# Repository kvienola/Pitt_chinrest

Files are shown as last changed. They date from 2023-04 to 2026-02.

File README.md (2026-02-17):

# A modular chinrest for retinal imaging

The main function of this repository is to distribute the component designs of the original chinrest. Everything is free to download and we only ask you to cite our paper XXX if you decide to use the chinrest design (or part of it) in your scientific setup.

The headrest was designed to be modular and most of the parts are 3D printable to minimize manufacturing costs. I roughly categorized the subassemblies/parts into few categories to quickly explain the reason behind the design decision and the material we chose. This is our first prototype so if you have ideas for design improvements, you can modify these parts as you please.

If you wish to have the master assembly file from Fusion 360, please contact Kari Vienola. Also if you find the chinrest files useful, consider citing our paper: http://dx.doi.org/10.1364/AO.513801 (Head stabilization apparatus for high-resolution ophthalmic imaging).

Kari V. Vienola  
_Academy Research Fellow_  
_University of Turku_

Ethan A. Rossi  
_Assistant Professor_  
_University of Pittsburgh_

## Contents

Detailed description of what is in each folder

### Mounting

As we are using Velmex motorized stages for all three axes of motion, the current base plate for mounting is quite large. The mounting plate size can be modified if you keep the hole distances in the bottom the same. The two mounting brackets are made from aluminum mainly so that they can be securely mounted to the base with threaded holes.

Material used: MIC6 cast aluminum, ½” thickness

### Chinrest

This consists of two parts, the sliding guide that is mounted to the base and the chinrest piece itself. The chinrest piece was designed to be moved along the z-axis (parallel to the optical axis of the incoming beam) to accommodate different head shapes. The “cupping” for the chin was done by trial and error and it can be altered if needed. Gluing a thin rubber in the chin cup will increase the friction as some 3D printed plastics might be a bit slippery. The bottom has a slot insert for metal piece that is inserted either a) gluing or b) heating up the metal piece and allowing the surrounding plastic to melt. This metal piece is meant to protect the plastic from the locking screw (not mandatory but highly suggested). The length of the dove rail can be easily extended by extruding the piece itself.

Material/parts used: standard 3D printing plastics and scrap metal/aluminum for the slot, brass insert: https://www.mcmaster.com/93738A210/

### Headband

The left and right mounting brackets have t-slots machined in them with slot opening for the screw to tighten the headband to a certain height. The adapter pieces that go inside the t-slot and the headband itself can be 3D printed as one piece but as we were prototyping, we kept them separate in case material had to be changed or the headband diameter would not be correct.
Brass inserts are melted into the headband for proper threads and the bottom hole are used for connecting the t-slot pieces with the headband. The top holes are for the screw that goes through the mounting bracket and locks the headband in place for the desired height.
Materials used: standard 3D printing plastic, brass inserts, screws to clock the band in place

### Forehead slider
The forehead slider consists of 4 pieces: tapered nut, the slider itself, the rod and the temple pad. Originally the idea was to machine the rod, but 3D printed version seemed to work just fine. The tapered nut will squeeze the rod opening the more you tighten it and provides very sturdy locking mechanism. The temple pad is just snapped in place and again, rubber or felt can be glued on to the surface if wanted.

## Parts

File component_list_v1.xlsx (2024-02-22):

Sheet: 3D printed parts
Item | Code | Qty | Printing Material
Tapered nut | RL001 | 2 | Depends on your 3D printer capabilities.
Forehead slider | RL002 | 2
Temple pad | RL003 | 2
Temple pad rod | RL004 | 2
Forehead band | RL005 | 1
Chinrest cup | RL006 | 1
Chinrest slider base | RL007 | 1
T-slot adapters | RL008 | 2

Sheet: CNC machined components
Item | Code | Qty | Material
Mounting bracket left | RL009 | 1 | Aluminum (MICA)
Mounting bracket right | RL010 | 1 | Aluminum (MICA)
Mounting base (custom) | RL011 | 1 | Aluminum (MICA)
Chinrest slider protection | RL012 | 1 | Aluminum (MICA)

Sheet: Off-the-shelf components
Item | McMaster & Carr code | Qty | Material | Usage | Link
Heat-Set Inserts for Plastic | 93738A210 | 5 | Brass | T-slot adapters and chinrest guide | https://www.mcmaster.com/93738A210/
Flat Head Screws | 92210A305 | 2 | Stainless Steel | To attach T-slot adapter to headband | https://www.mcmaster.com/92210A305/
Socket Head Screw | 92196A291 | 2 | Stainless Steel | Clamp headband in place | https://www.mcmaster.com/92196A291/
Srew-Head Mount Knob | 94052A051 | 2 | Plastic | Knob for the headband clamp | https://www.mcmaster.com/94052A051/
Socket Head Screw | 92196A541 | X | Stainless Steel | Universal component mounting (chinrest, vertical brackets) | https://www.mcmaster.com/92196A541/
The length of each component presented here can vary in case you decide to alter the design.
You may also use screws that you have already or different type of plastic inserts.

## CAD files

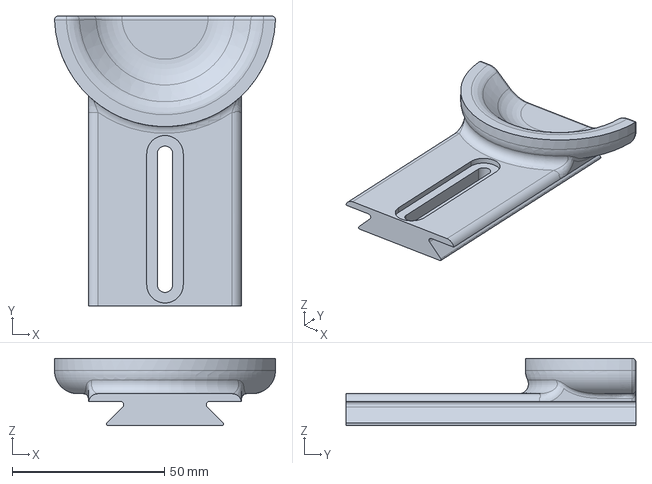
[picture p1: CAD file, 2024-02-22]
chinrest/version_02/chinrest_cup.step
72.6 x 95.2 x 22.1 mm

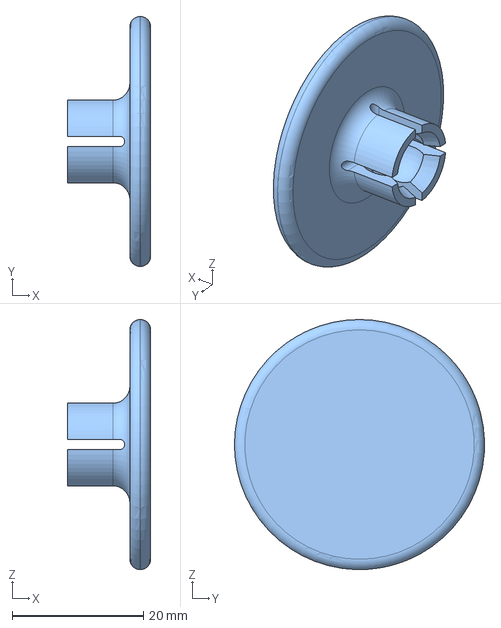
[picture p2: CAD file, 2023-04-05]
forehead slider/temple_pad.step
12.7 x 38.1 x 38.1 mm

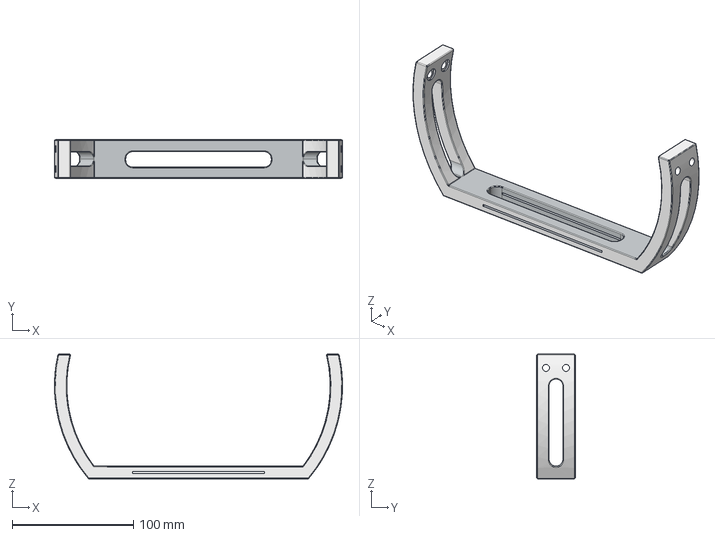
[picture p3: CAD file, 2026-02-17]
headband/headband_Davis_v1.stp
237.5 x 31.8 x 102.7 mm

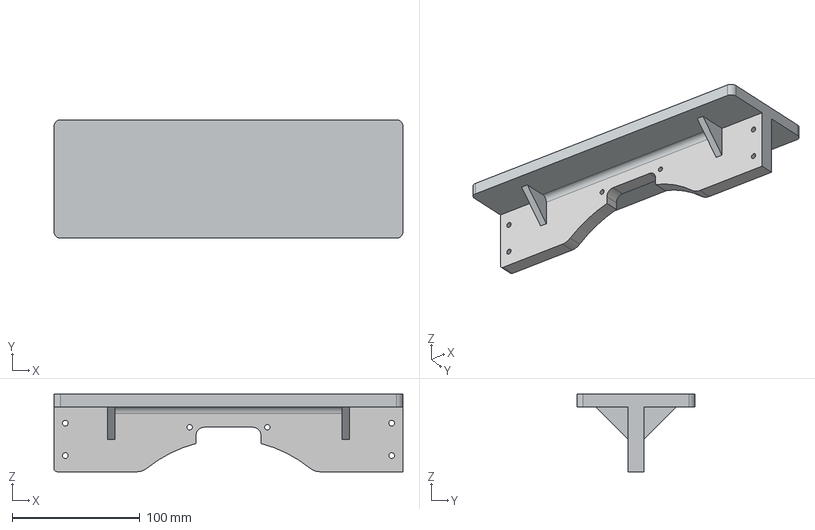
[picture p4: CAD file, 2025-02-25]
mounting/mounting_base_AOSLO_ver2.stp
273.6 x 92.7 x 60.8 mm

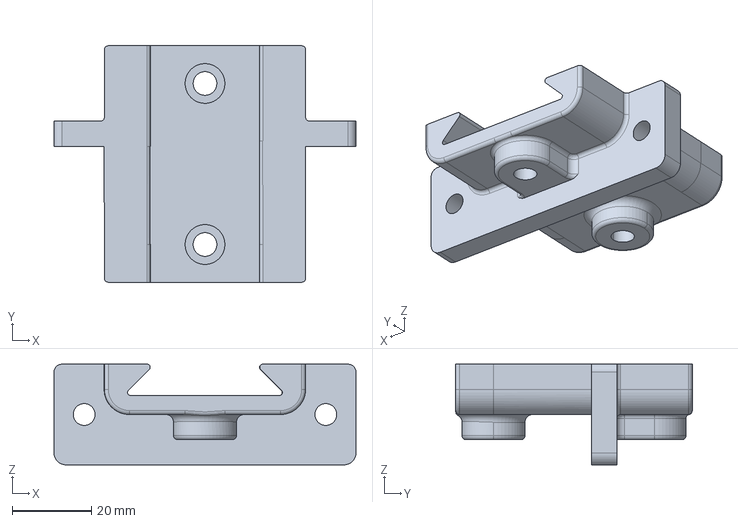
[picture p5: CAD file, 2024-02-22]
chinrest/version_02/chinrest_slider.step
76.2 x 59.7 x 25.4 mm

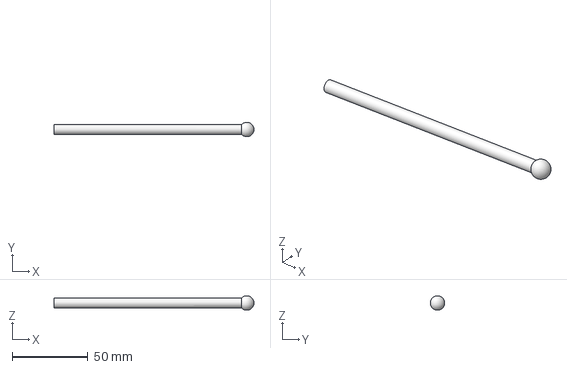
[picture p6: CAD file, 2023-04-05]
forehead slider/slider_rod.step
131.7 x 9.49 x 9.53 mm

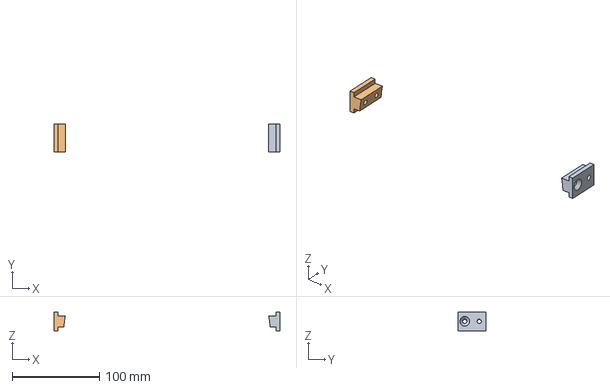
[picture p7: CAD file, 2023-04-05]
headband/detachable_tslots.step
259.7 x 31.8 x 21.6 mm

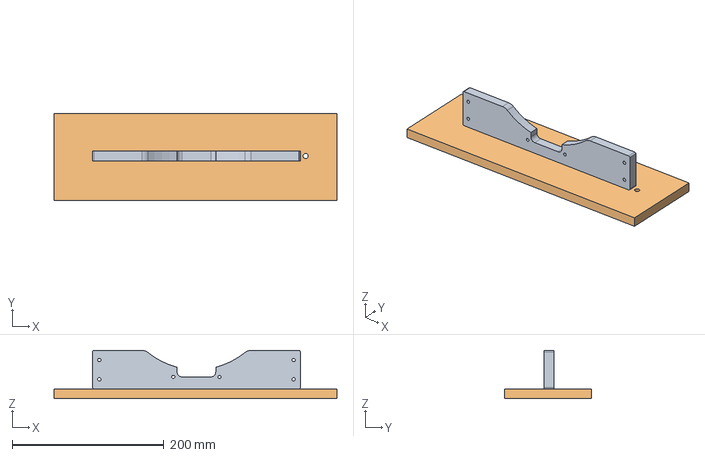
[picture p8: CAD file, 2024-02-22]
mounting/mounting_base_Tracker.step
372.6 x 114.3 x 63.5 mm

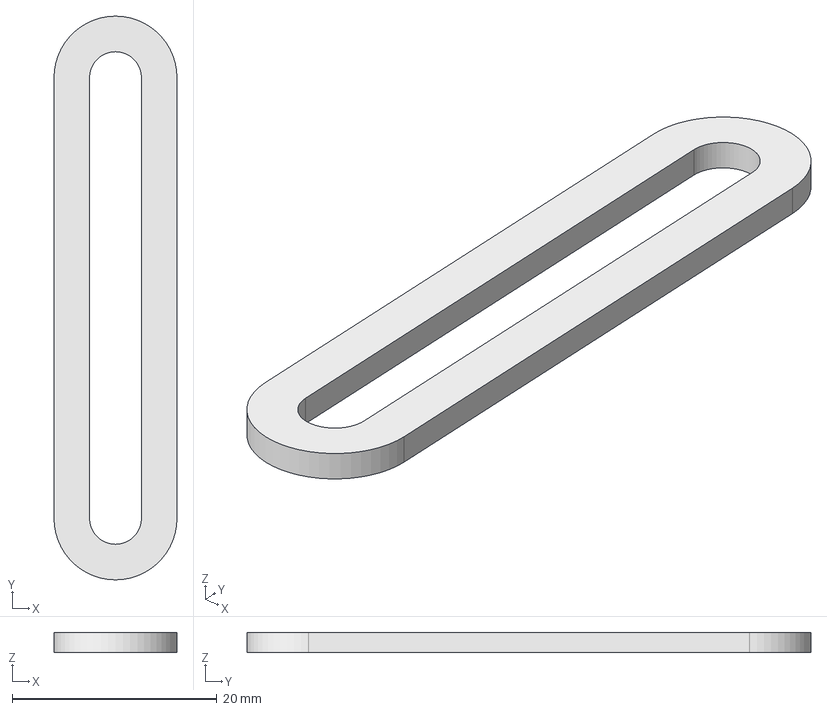
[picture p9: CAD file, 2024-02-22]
chinrest/version_02/metal_insert.step
12.0 x 55.0 x 2.00 mm

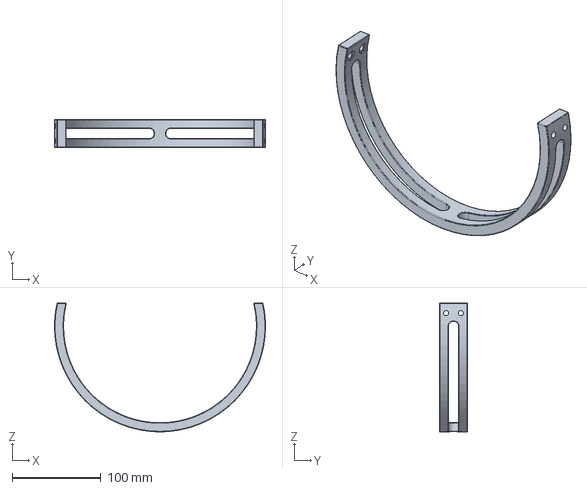
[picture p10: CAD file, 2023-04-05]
headband/headband.step
237.5 x 31.8 x 144.9 mm

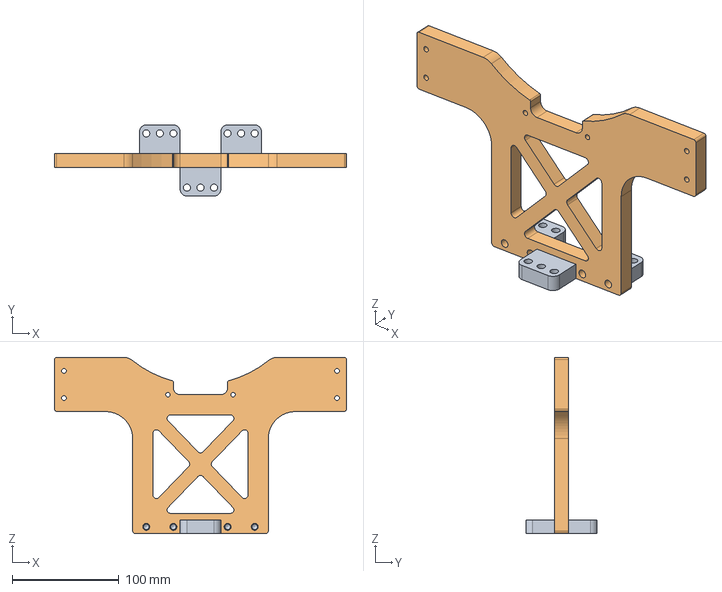
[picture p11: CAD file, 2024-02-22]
mounting/mounting_base_FFOCT.step
273.6 x 66.7 x 165.1 mm
V4 Riser Bracket x 3

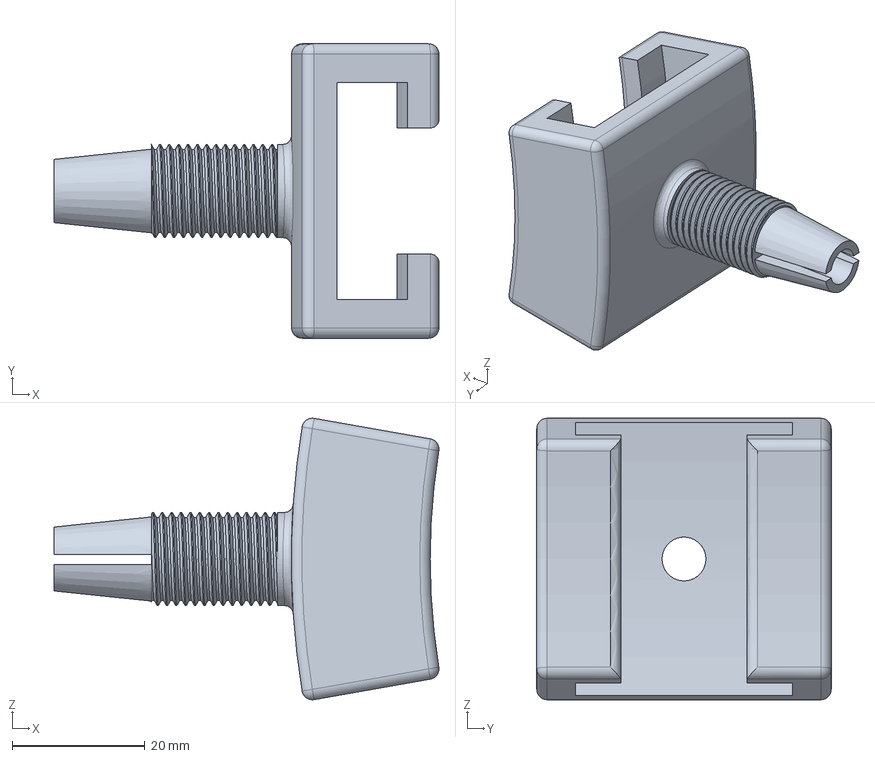
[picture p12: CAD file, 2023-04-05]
forehead slider/slider.step
58.1 x 44.4 x 42.5 mm

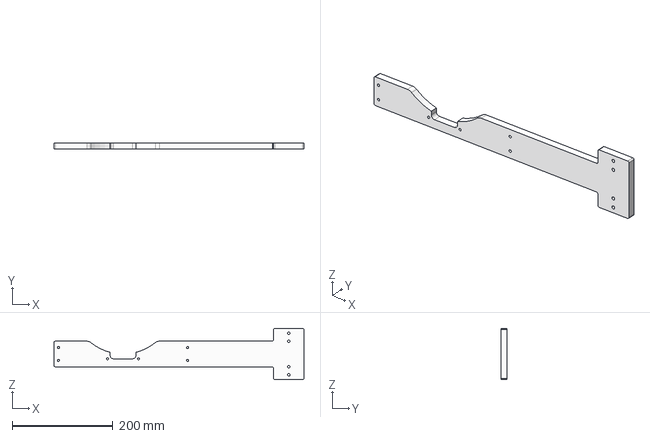
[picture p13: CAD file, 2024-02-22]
mounting/mounting_base_LDH.step
495.3 x 12.7 x 101.6 mm

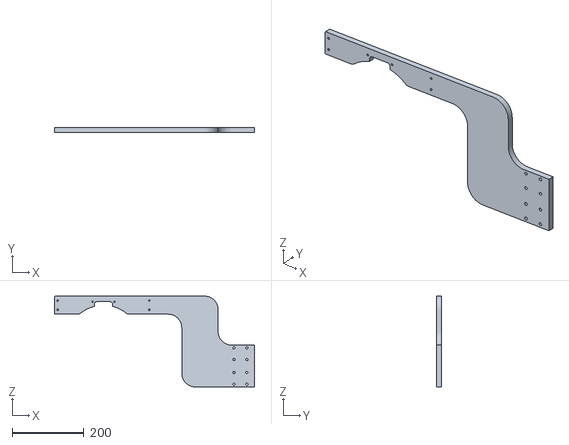
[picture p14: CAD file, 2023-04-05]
mounting/mounting_base.stl
558.8 x 12.7 x 254.0

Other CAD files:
mounting/right_bracket.step
mounting/mounting_base_AOSLO.step
mounting/left_bracket.step
forehead slider/tapered_nut.step
chinrest/version_01/chinrest_cup.step
chinrest/version_01/chinrest_cup.stl
chinrest/version_01/chinrest_sliderbase.step
chinrest/version_01/chinrest_sliderbase.stl
chinrest/version_01/metal_insert.step
chinrest/version_02/chinrest_cup.stl
chinrest/version_02/chinrest_slider.stl
forehead slider/forehead_slider_assembly.f3d
forehead slider/slider.stl
forehead slider/slider_rod.stl
forehead slider/tapered_nut.stl
forehead slider/temple_pad.stl
headband/detachable_tslots.stl
headband/headband.stl
headband/headband_Davis_v1.stl
mounting/left_bracket.stl
mounting/mounting_base_AOSLO_ver2.stl
mounting/right_bracket.stl

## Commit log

2024-02-22 Delete chinrest/Barbed brass insert for plastic.txt
    New version coming up
2024-02-22 Delete chinrest directory
    Adding new versions of chinrest to the repository
    [chinrest_piece.step, chinrest_piece.stl, chinrest_sliding_module.step, chinrest_sliding_module.stl]
2026-02-17 Add files via upload
    New headband design for FreezEye eye tracker in UC Davis. Due to limited space the circular headband was flattened.
    [headband_Davis_v1.stl, headband_Davis_v1.stp]
